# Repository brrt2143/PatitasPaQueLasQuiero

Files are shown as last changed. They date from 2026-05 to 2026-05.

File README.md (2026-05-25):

# Pata de Paloma V4 — Prótesis de Miembro Inferior para Columbiformes

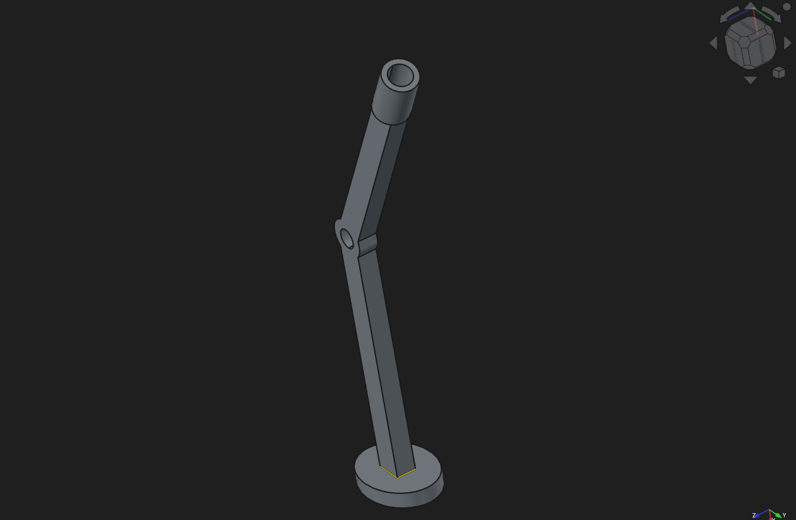
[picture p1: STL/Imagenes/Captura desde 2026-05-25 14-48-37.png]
Modelo isométrico


**Simulación vertical (2.4 N)**

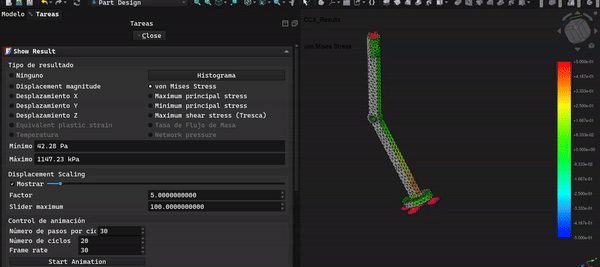
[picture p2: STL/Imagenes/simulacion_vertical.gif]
Simulación vertical


**Simulación horizontal (2.4 N)**

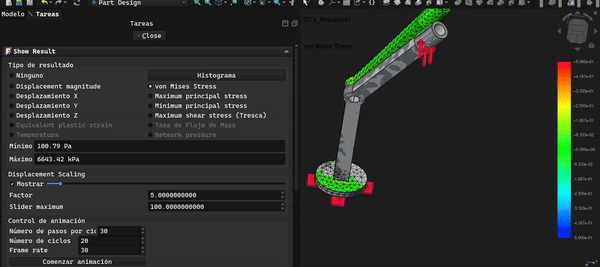
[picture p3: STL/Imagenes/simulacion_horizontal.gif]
Simulación horizontal


Prótesis de pie/pierna para palomas (*Columba livia*) con amputación de miembro inferior, diseñada para impresión 3D en PETG y validada mediante análisis de elementos finitos (FEM) con CalculiX.

---

## Descripción

Este proyecto propone una prótesis de una sola pieza imprimible en PETG que replica la geometría funcional del miembro inferior de una paloma doméstica: socket de fijación, tibiotarso, articulación tibiotarsal, tarsometatarso, nervadura estructural y planta del pie.

El diseño está orientado a rehabilitadores de fauna y veterinarios con acceso a impresoras FDM. No requiere ensamble de piezas móviles en su versión completa.

---

## Archivos

```
STL/
├── Fusion004.stl                       — Pieza completa (impresión en una sola vez)
└── partes/
    ├── ExtrusionSocket.stl             — Socket de fijación al muñón
    ├── ExtrusionTibiotarso.stl         — Segmento tibial
    ├── ExtrusionArticulacion.stl       — Articulación tibiotarsal
    ├── ExtrusionTarsometatarso.stl     — Segmento metatarsal
    ├── ExtrusionNervadura.stl          — Nervadura estructural
    └── ExtrusionPlanta.stl             — Planta del pie

FreeCAD/
└── Pata_de_PalomaV4.1.FCStd           — Archivo fuente editable
```

---

## Impresión

| Parámetro | Valor recomendado |
|---|---|
| Material | PETG |
| Relleno | 100% |
| Soporte | No requerido (pieza completa) |
| Temperatura boquilla | 230–240 °C |
| Temperatura cama | 70–80 °C |

---

## Validación estructural (FEM)

Simulación realizada en FreeCAD 1.1.1 + CalculiX. Material: PETG (E = 3150 MPa, Poisson = 0.38). Límite de fluencia de referencia: ~50 MPa.

### Carga vertical (eje Z) — escenario de apoyo normal

| Carga | Von Mises máx | Desplazamiento máx | Factor de seguridad |
|---|---|---|---|
| 0.6 N (reposo) | 0.287 MPa | 0.097 mm | ~174× |
| 2.4 N (carga máx) | 1.15 MPa | 0.39 mm | ~43× |

### Carga lateral (eje X) — escenario de impacto lateral

| Carga | Von Mises máx | Desplazamiento máx | Factor de seguridad |
|---|---|---|---|
| 0.6 N | 1.66 MPa | 0.72 mm | ~30× |
| 2.4 N | 6.64 MPa | 2.86 mm | ~7.5× |

### Carga frontal (eje Y) — escenario de frenado

| Carga | Von Mises máx | Desplazamiento máx | Factor de seguridad |
|---|---|---|---|
| 0.6 N | 1.054 MPa | 0.55 mm | ~47× |
| 2.4 N | 4.22 MPa | 2.20 mm | ~12× |

### Sensibilidad al módulo de Young

| E (MPa) | Von Mises máx | Desplazamiento máx |
|---|---|---|
| 3150 (PETG estándar) | 0.287 MPa | 0.097 mm |
| 2100 (PETG menor calidad) | 0.287 MPa | 0.150 mm |

Los esfuerzos no varían con E (comportamiento elástico lineal esperado). El diseño es robusto ante variación de calidad del filamento.

---

## Mejoras posibles

### Articulación en TPU (no probado)
Es posible sustituir la pieza `ExtrusionArticulacion.stl` por una versión impresa en TPU para mejorar la elasticidad y absorción de impactos en la articulación tibiotarsal. Esta modificación **no ha sido simulada ni probada** por limitaciones computacionales — se incluye como sugerencia para quienes quieran iterar sobre el diseño.

---

## Limitaciones conocidas

- Diseño mono-material (PETG). Una versión multi-material con TPU mejoraría la amortiguación general, pero requiere simulación adicional.
- No incluye dedo posterior (hallux). El diseño se limita a la estructura de apoyo principal.
- No ha sido probado en animales reales. Los resultados FEM son teóricos bajo condiciones estáticas lineales.

---

## Materiales y herramientas utilizadas

- FreeCAD 1.1.1
- CalculiX (solver FEM incluido en FreeCAD)
- PETG como material de referencia

---

## Licencia

[Creative Commons Attribution 4.0 International (CC BY 4.0)](https://creativecommons.org/licenses/by/4.0/)

Puedes usar, modificar y distribuir este diseño libremente con atribución al autor original. Esta licencia aplica a todos los archivos STL y FreeCAD del repositorio.

---

## Apoya el proyecto

Si este proyecto te fue útil, puedes apoyar su desarrollo:



Este proyecto fue desarrollado con [FreeCAD](https://www.freecad.org/), software libre y de código abierto. Si lo usas, considera apoyar su desarrollo en [freecad.org/donate](https://www.freecad.org/donate.php).

---

## Autor

Brayan ([@brrt2143](https://github.com/brrt2143)) — Ciudad Juárez / Chihuahua, México  
Ingeniería Biomédica

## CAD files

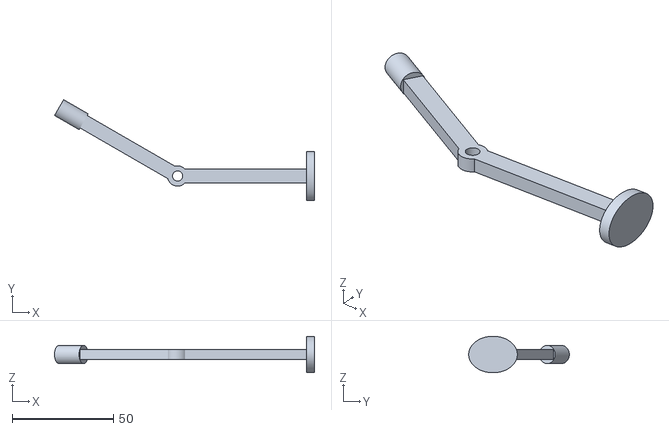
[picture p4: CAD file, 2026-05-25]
STL/completo/Pata de PalomaV4 -Fusion004.stl
128.3 x 49.7 x 18.0

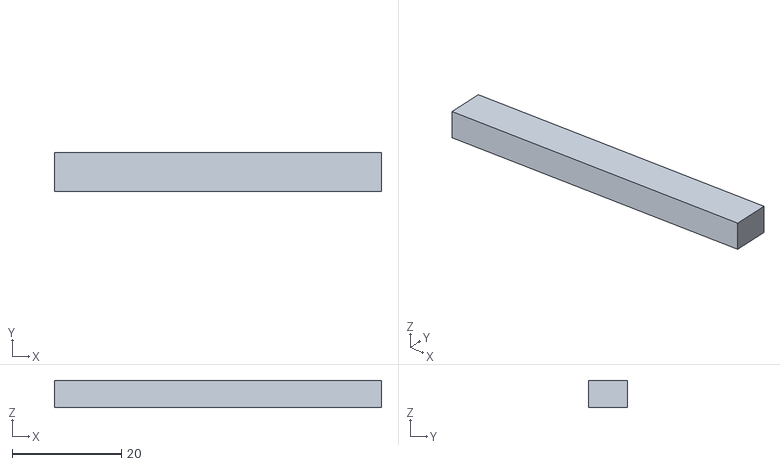
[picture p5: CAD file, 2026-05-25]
STL/partes/Pata de PalomaV4 -ExtrusionTarsometatarso.stl
60.0 x 7.07 x 5.00

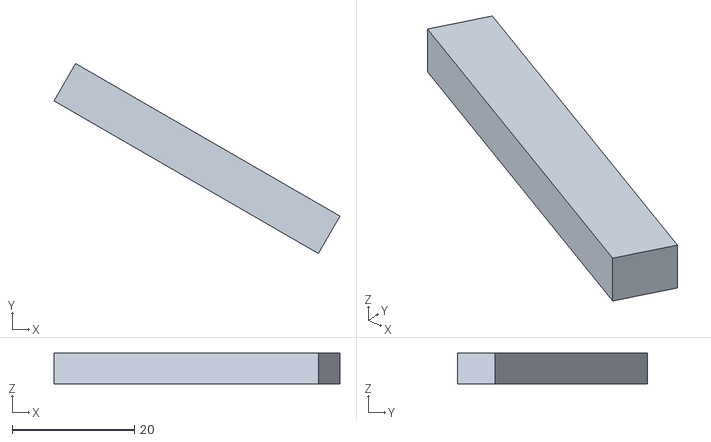
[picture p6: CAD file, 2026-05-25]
STL/partes/Pata de PalomaV4 -ExtrusionTibiotarso.stl
46.8 x 31.1 x 5.00

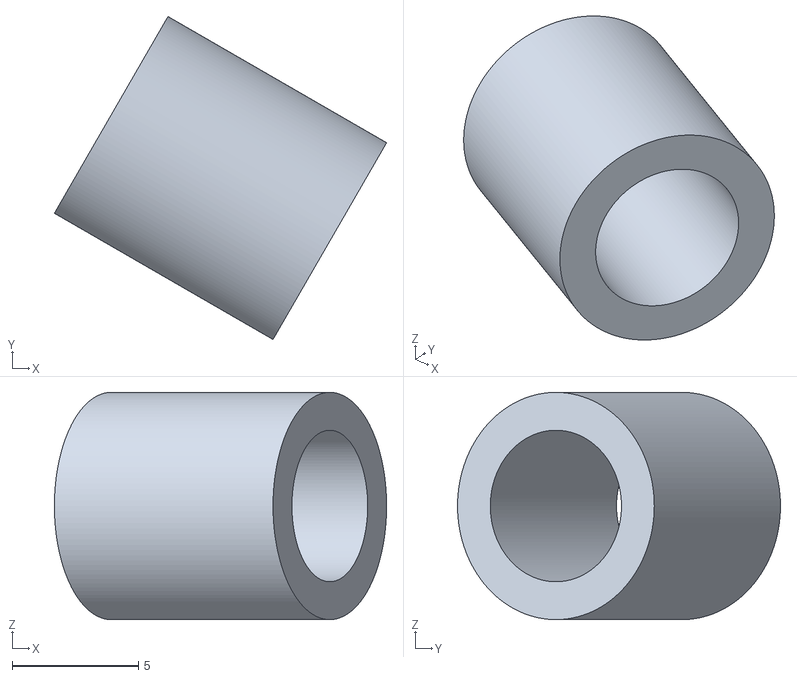
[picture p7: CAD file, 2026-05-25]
STL/partes/Pata de PalomaV4 -ExtrusionNervadura.stl
13.2 x 12.8 x 9.00

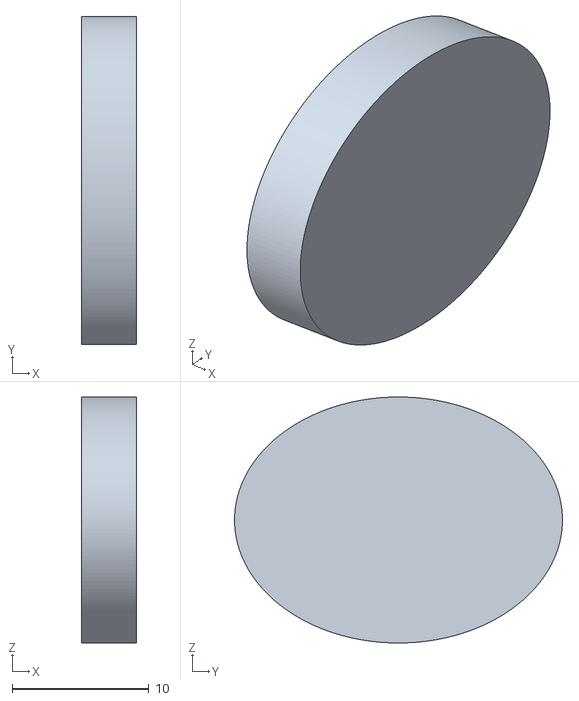
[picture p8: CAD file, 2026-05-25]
STL/partes/Pata de PalomaV4 -ExtrusionPlanta.stl
4.00 x 24.0 x 18.0

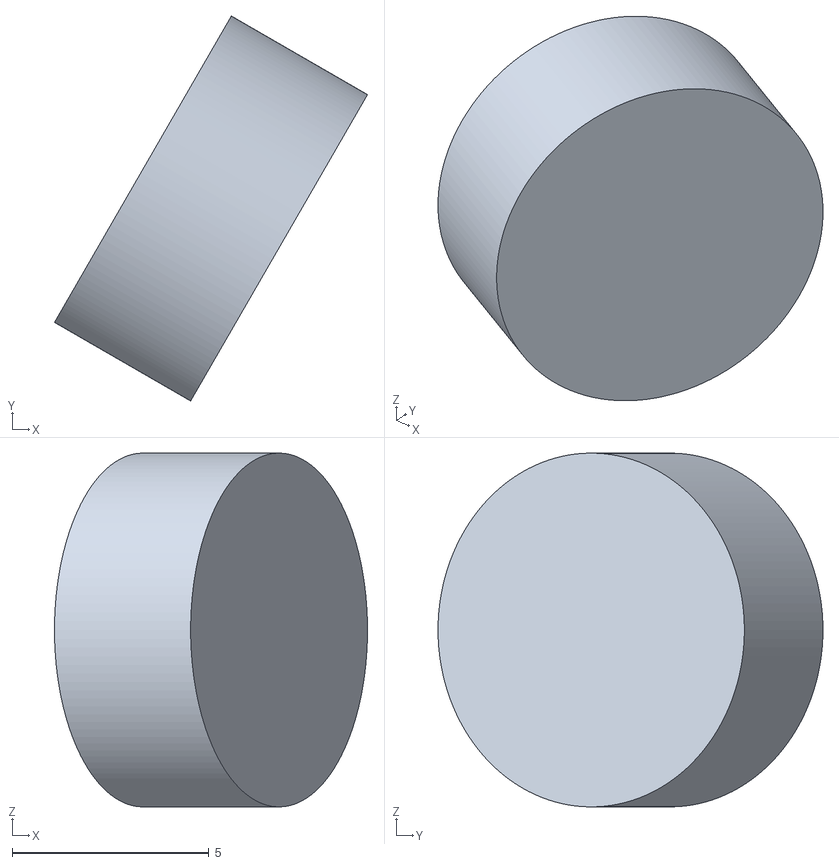
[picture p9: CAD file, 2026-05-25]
STL/partes/Pata de PalomaV4 -ExtrusionSocket.stl
7.96 x 9.79 x 9.00

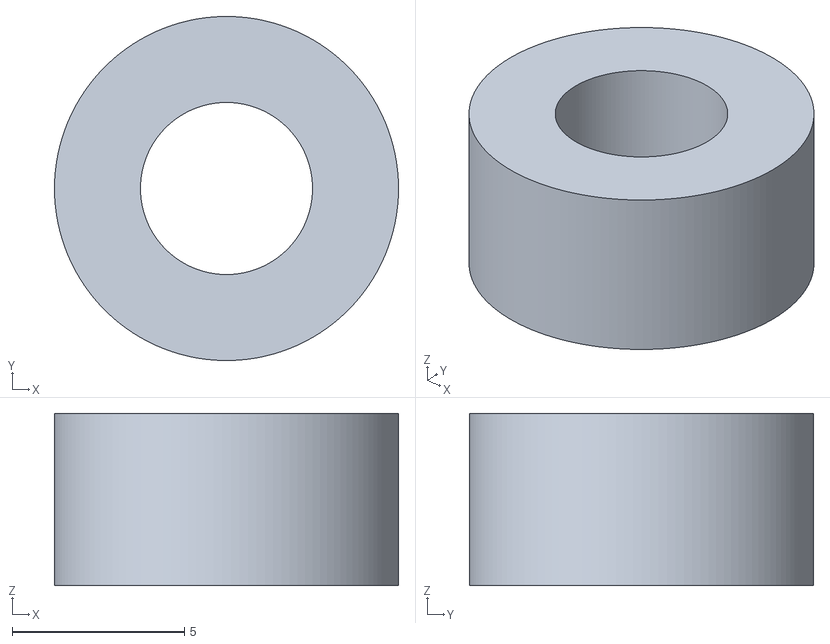
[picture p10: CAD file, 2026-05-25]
STL/partes/Pata de PalomaV4 -ExtrusionArticulación.stl
10.0 x 10.00 x 5.00

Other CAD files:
STL/FreeCAD/Pata de PalomaV4.1.FCStd
